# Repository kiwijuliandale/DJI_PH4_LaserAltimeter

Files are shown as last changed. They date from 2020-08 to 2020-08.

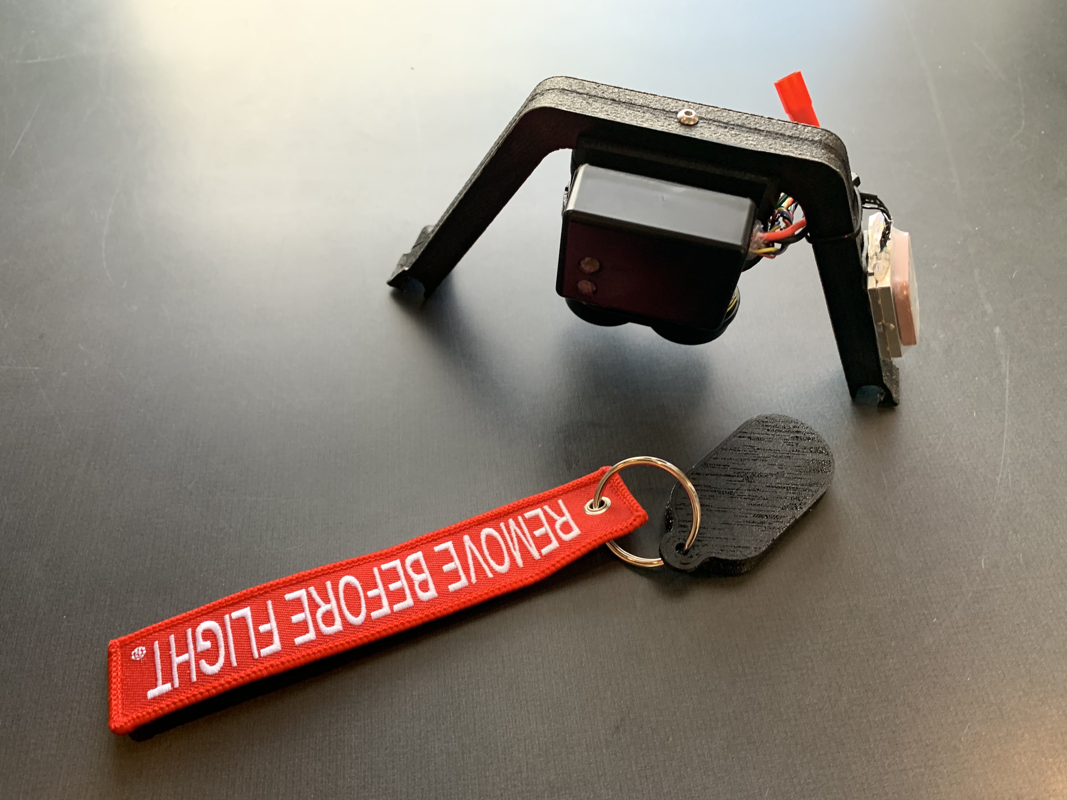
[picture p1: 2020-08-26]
Assembly/IMG_0025.jpeg

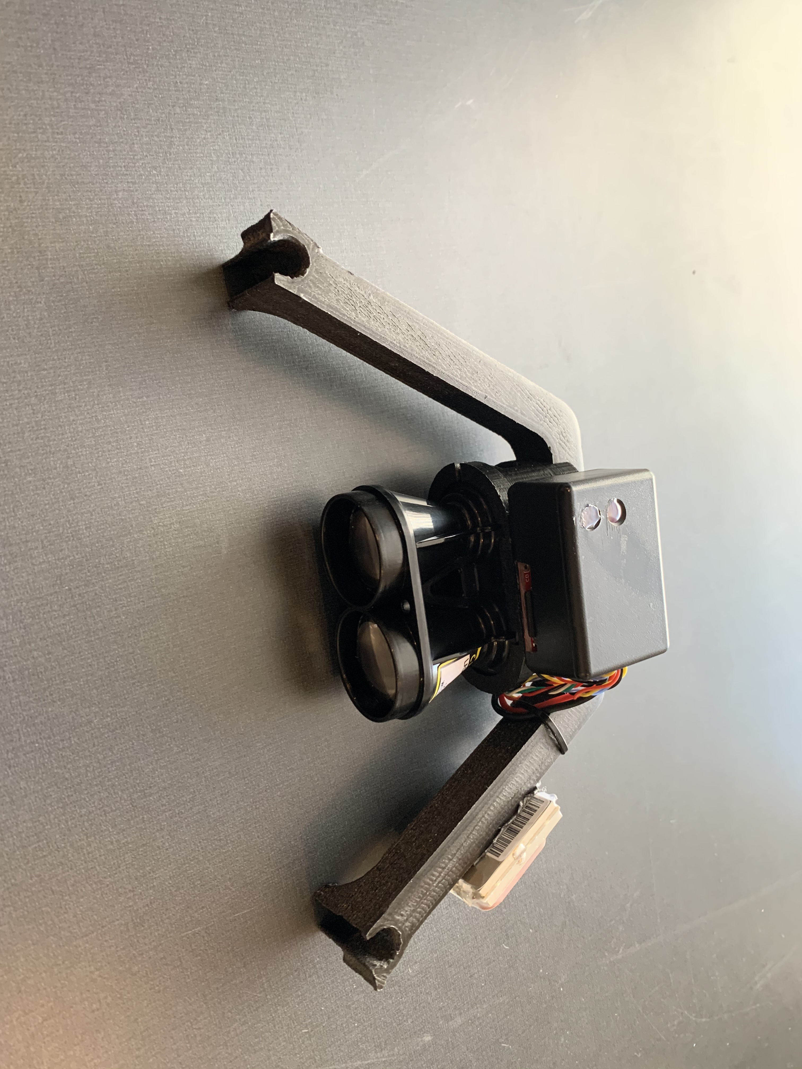
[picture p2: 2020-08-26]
Assembly/IMG_0023.jpeg

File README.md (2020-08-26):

# DJI Phantom 3/4 laser altimeter installation

Before we begin, there are some important warnings…

**WARNING** 
Modifying the DJI will void any warranties and could damage the aircraft. Only perform these modifications if you have adequate technical skills to 
perform the modifications.

**Disclaimer** 
The information provided by [Julian Dale or Duke University MaRRS Lab] (“we,” “us” or “our”) on [marineuas.net or Github/marrs-lab] (the “Site”) is for general informational purposes only. All information on the Site is provided in good faith, however we make no representation or warranty of any kind, express or implied, regarding the accuracy, adequacy, validity, reliability, availability or completeness of any information on the Site.

Under no circumstance shall we have any liability to you for any loss or damage of any kind incurred as a result of the use of the site or reliance on any information provided on the site. Your use of the site and your reliance on any information on the site is solely at your own risk. 

About the information included:

>I have included a tutorial video on how to install the power feed from the DJI battery. (By no means my best work but should provide the necessary information!!)
This allows the laser to power from the aircraft and will automatically start when the aircraft powers up. This saves weight and the risk of a separate power supply going flat. If you feel at all uncomfortable disassembling your aircraft, then use an external USB power bank or small LiPo battery. Please find the video tutorial here https://vimeo.com/451298704 

There are three folders containing ;

| Folder | Description |
| ------ | ------ |
| 3D Printer Files | STL's for printing the mouting frame |
| Arduino Code | Arduino code and libraries for the sensors. I have included the instructions from Steve Dawson & Hamish Bowman’s (Departments of Marine Science and Geology, University of Otago, Dunedin New Zealand) This is all their work and code and I have just included this as a reference |
| Assembly | Some assembly images and references. We have been using modified SF11C laser settings with good results over the water. Information on these settings are included in the assembly folder |

**Making Photogrammetry measurements:**
Because the laser altimeter is measuring a hypotenuse length, you need to calculate the vertical distance with a basic trig function. This can be done in excel.
Once this is done, KC Bierlich, Walter Torres and Clara Bird have developed some amazing tools for making the measurements in MorhhometriX and Collatrix for collating the data outputs. 
https://github.com/wingtorres/morphometrix
https://github.com/cbirdferrer/collatrix

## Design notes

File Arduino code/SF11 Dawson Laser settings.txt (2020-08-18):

     b: Zero datum offset ........ 0.00 m
     c: Measuring mode ........... long range
  ------------------------------------
  d: Hide communication menu
     e: Serial port baud rate..... 19200
     f: Serial output mode........ continuous
     g: I2C bus address........... 0x55
     s: Pixhawk I2C compatability. on
  ------------------------------------
  h: Show analog and alarm menu
  ------------------------------------
  m: Show filter menu
  ------------------------------------
  s: Show advanced menu
  ------------------------------------

     *** SF11/C V9 Firmware: V1.5.0 ***
            Serial: S11-16588

  ------------------------------------
  a: Hide system menu
     b: Zero datum offset ........ 0.00 m
     c: Measuring mode ........... long range
  ------------------------------------
  d: Hide communication menu
     e: Serial port baud rate..... 19200
     f: Serial output mode........ continuous
     g: I2C bus address........... 0x55
     s: Pixhawk I2C compatability. on
  ------------------------------------
  h: Hide analog and alarm menu
     i: Linear analog output...... 0.00 m to 25.00 m = 0.00 V to 2.048 V
     j: Analog distance range..... 0.00 m to 25.00 m
     k: Analog voltage range...... 0.00 V to 2.048 V
  ------------------------------------
  m: Show filter menu
  ------------------------------------
  s: Show advanced menu
  ------------------------------------

     *** SF11/C V9 Firmware: V1.5.0 ***
            Serial: S11-16588

  ------------------------------------
  a: Hide system menu
     b: Zero datum offset ........ 0.00 m
     c: Measuring mode ........... long range
  ------------------------------------
  d: Hide communication menu
     e: Serial port baud rate..... 19200
     f: Serial output mode........ continuous
     g: I2C bus address........... 0x55
     s: Pixhawk I2C compatability. on
  ------------------------------------
  h: Hide analog and alarm menu
     i: Linear analog output...... 0.00 m to 25.00 m = 0.00 V to 2.048 V
     j: Analog distance range..... 0.00 m to 25.00 m
     k: Analog voltage range...... 0.00 V to 2.048 V
  ------------------------------------
  m: Hide filter menu
     n: Output on lost signal..... 130.00 m
        p: Confirm lost signal.... 1.0 seconds
     q: Median filter............. on
        r: Median filter size..... 16 results
  ------------------------------------
  s: Show advanced menu
  ------------------------------------

     *** SF11/C V9 Firmware: V1.5.0 ***
            Serial: S11-16588

  ------------------------------------
  a: Hide system menu
     b: Zero datum offset ........ 0.00 m
     c: Measuring mode ........... long range
  ------------------------------------
  d: Hide communication menu
     e: Serial port baud rate..... 19200
     f: Serial output mode........ continuous
     g: I2C bus address........... 0x55
     s: Pixhawk I2C compatability. on
  ------------------------------------
  h: Hide analog and alarm menu
     i: Linear analog output...... 0.00 m to 25.00 m = 0.00 V to 2.048 V
     j: Analog distance range..... 0.00 m to 25.00 m
     k: Analog voltage range...... 0.00 V to 2.048 V
  ------------------------------------
  m: Hide filter menu
     n: Output on lost signal..... 130.00 m
        p: Confirm lost signal.... 1.0 seconds
     q: Median filter............. on
        r: Median filter size..... 16 results
  ------------------------------------
  s: Hide advanced menu
        t: Sensitivity offset..... 0
  ------------------------------------

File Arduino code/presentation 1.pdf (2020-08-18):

Building the LIDAR/GPS datalogger

This is a building guide intended as supplementary material to the manuscript “Inexpensive aerial photogrammetry for studies of whales and other large marine animals”. It is written to allow interested researchers to build the datalogger described in the manuscript. The building task is not difficult for anyone with reasonably good soldering skills.

Parts list
Item | Example supplier
Lightware SF11 lidar | www.lightware.co.za
3.3v 8MHz Pro Micro Arduino clone | www.sparkfun.com
3.3v ProMicro MicroSD transflash breakout | www.sparkfun.com
GlobalSat EM506 GPS module | www.sparkfun.com
Pololu MinIMU-9 v5 Gyro, Accel, Compass | www.nicegear.so.nz
DC-DC UBEC 5v 3a voltage regulator | www.mrpositive.co.nz
100µF capacitor | Any electronics store
microSD card | Any electronics store
7.4v 2cell LIPO batteries | Any R/C hobby store
Plus: wire, solder, heatshrink

The size and writing speed of the micro SD card are not critical, as the datalogger files are small (c.8kB/min).

You will need to figure out how long the cabling needs to be to suit your particular UAV and your preferred layout. You’ll also need to source appropriate plastic boxes to house the gps antenna and the datalogger. For the datalogger, we’ve used an Olympus microcassette box. A rubber band provides extra security to hold the lid shut.

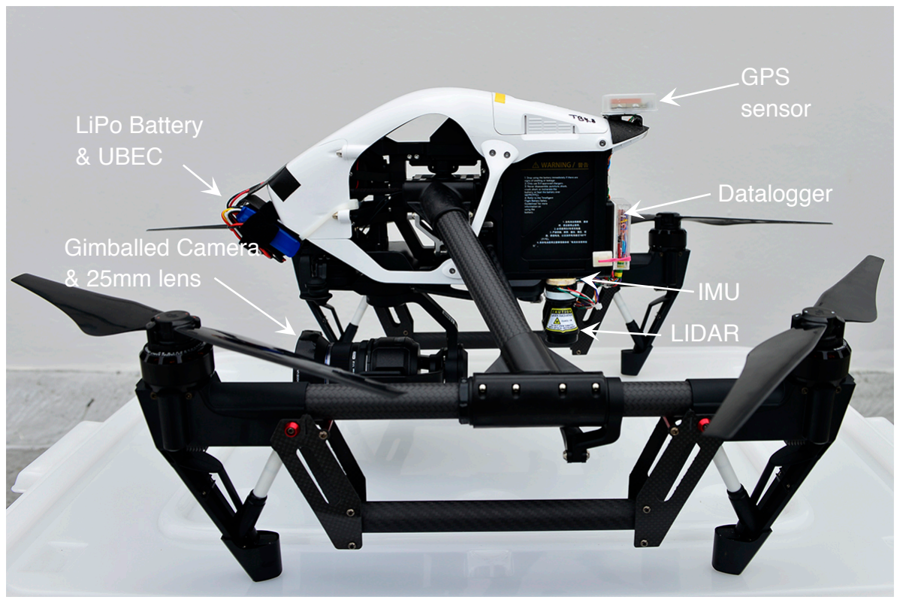
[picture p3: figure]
LiPo Battery & UBEC; GPS sensor; Datalogger; LIDAR; IMU; Gimballed Camera & 25mm lens

Layout of the datalogger components on the DJI Inspire 1Pro

Datalogger wiring diagram

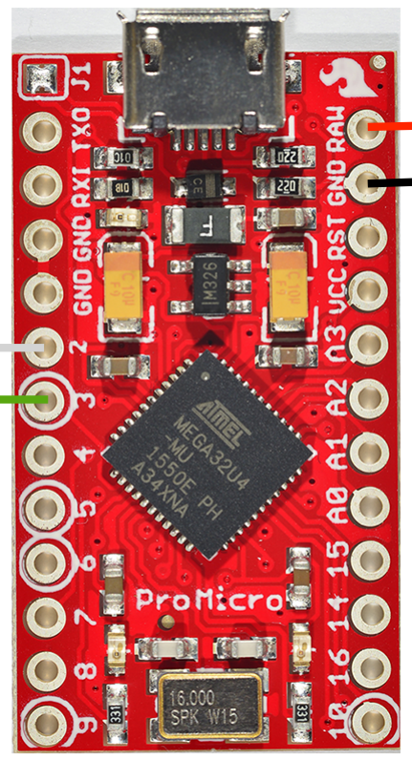
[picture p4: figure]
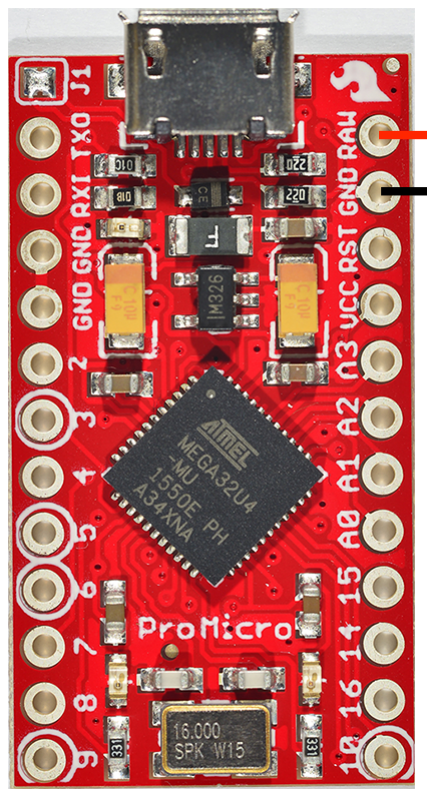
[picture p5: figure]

lidar
connector

UBEC +5v
UBEC Gnd

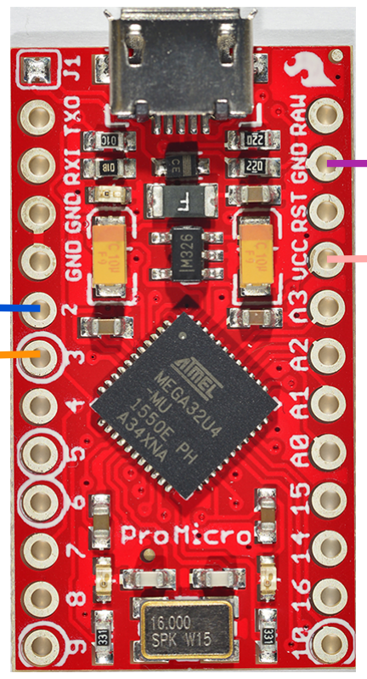
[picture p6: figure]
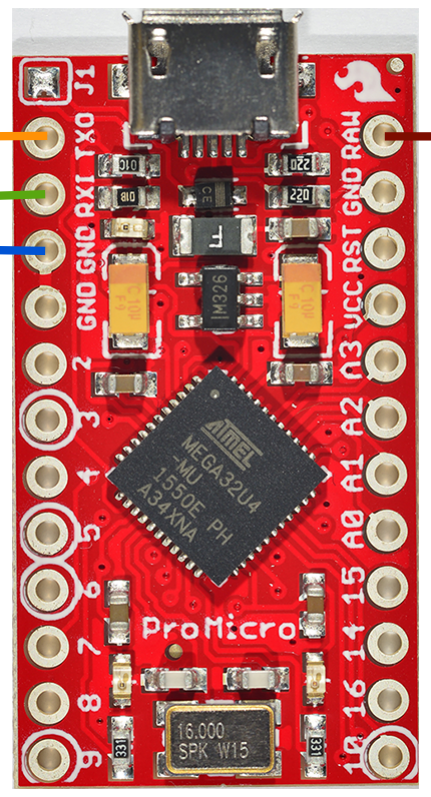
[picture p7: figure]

g
GPS
connector

MicroSD breakout

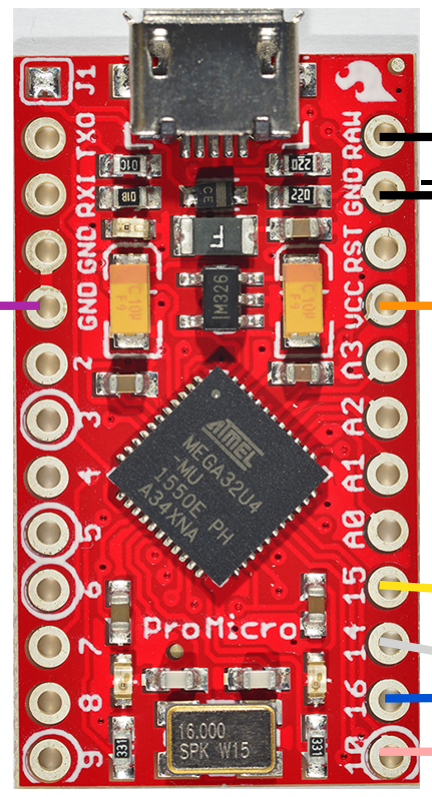
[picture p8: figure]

100µF -

MinIMU

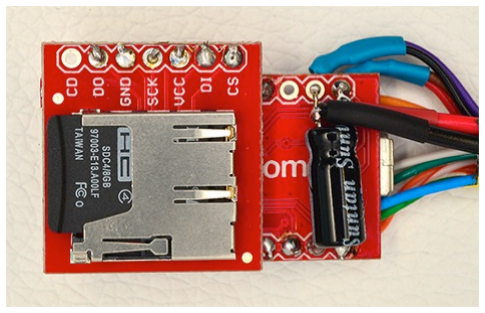
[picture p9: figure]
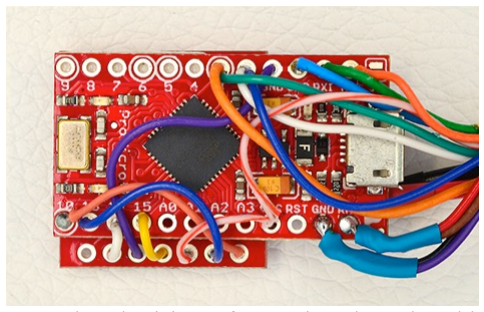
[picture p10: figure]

Completed wiring of ProMicro board and breakout

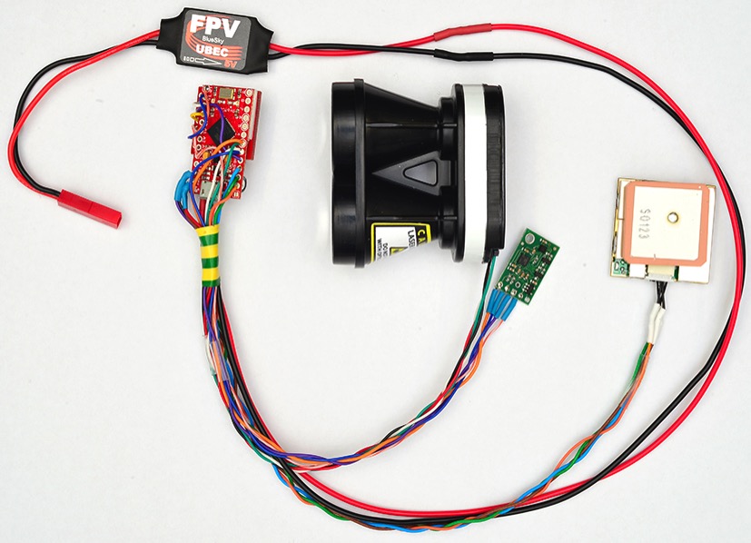
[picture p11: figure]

Completed assembly of component parts before attachment to UAV

Programming and setup of LiDAR + Datalogger

LiDAR setup (SF11C Laser Altimeter from Lightware Optoelectronics)
This needs to be set up using a micro-USB cable plugged in between your computer and the LiDAR unit. You will need a terminal program to do this, examples are the vendor-supplied Lightware Terminal on MS Windows, Zterm on Mac OS, or GTKTerm on Linux.

http://www.dalverson.com/zterm/
https://sourceforge.net/projects/gtkterm/

You will need to connect to the appropriate serial/COM port as created by the USB connection. If in doubt try several from the list. If using Z-Term, connect the cable to the lidar and plug it in to your computer before you start Z-term, Under Settings/Modem Preferences choose the “usbserial….” port, and under Settings/Connection set baud rate to 115200 (8 bits 1 stop bit). You should see a live stream of data. If not, try changing the baud rate.

Pressing the space bar stops the live stream, and brings up the LiDAR setup menu. Input the following settings. Press the appropriate letter to expand the menu.

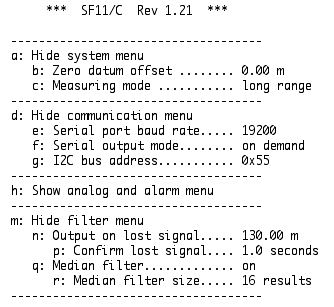
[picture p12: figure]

For the median filter we use a window size of 16. As the device samples at 16 Hz this corresponds to a 1 second filter window. This setting makes the lidar much less sensitive to momentary interruptions of the beam, and produces far fewer outliers.

Serial baud rate (d, e) is not relevant. The I2C protocol (d, g) is crucial.

Arduino software
We used the Arduino IDE software version 1.6.12 with a SparkFun 3.3v ProMicro Arduino board

In the Tools menu go to: Tools -> Board -> Board manager...

Find "SparkFun AVR Boards" and click install.

After that finished, in the Tools menu go to:
Tools -> Board -> SparkFun Pro Micro
Tools -> Processor -> ATmega32U4 (3.3V, 8 MHz)
Tools -> Port -> (select appropriate value once it is plugged in)

It is important that the correct values are set for the above.

You will need to install the TinyGPS++ processing library from http://arduiniana.org/libraries/tinygpsplus/
Follow the instructions on the website to download the library andinstall it into your Arduino "libraries" folder.

For inclinometer support using the Pololu MinIMU-9 board, install the LSM6 library
from https://github.com/pololu/lsm6-arduino
Follow the instructions on the website to download the library and install it into your Arduino "libraries" folder.

With the drone_GPS_and_LiDAR_logger_with_accel.ino and support_fns.ino files installed in a folder named "drone_GPS_and_LiDAR_logger_with_accel" within your Arduino "sketchbook" folder, select File -> Open in the Arduino IDE and then run Sketch -> Verify/Compile. An error will occur if the wrong family of Arduino board is selected or if it can't find the support libraries where it expects to find them on the hard drive.

Finally, with the Arduino connected and the appropriate serial Port selected from the Tools menu, select Sketch -> Upload. This will re-compile the code and upload it via the USB cable. Lights on the Arduino will blink during the process. When it is complete the words "Done uploading." will appear near the bottom of the Arduino software window.

To test, select Tools -> Serial Monitor from the menu. New data will only be
output when a valid GPS fix is in place.

Before Installation on the UAV we glue the flat side of IMU to the rear of the lidar, and make up a lightweight spacer to glue the LIDAR underneath the UAV. We attempt to do this as near to the centre of balance as we can.

Installation on the UAV
We made carbon fibre brackets for the GPS sensor and to hold the battery and UBEC on the I1P. Something less sophisticated should suffice.

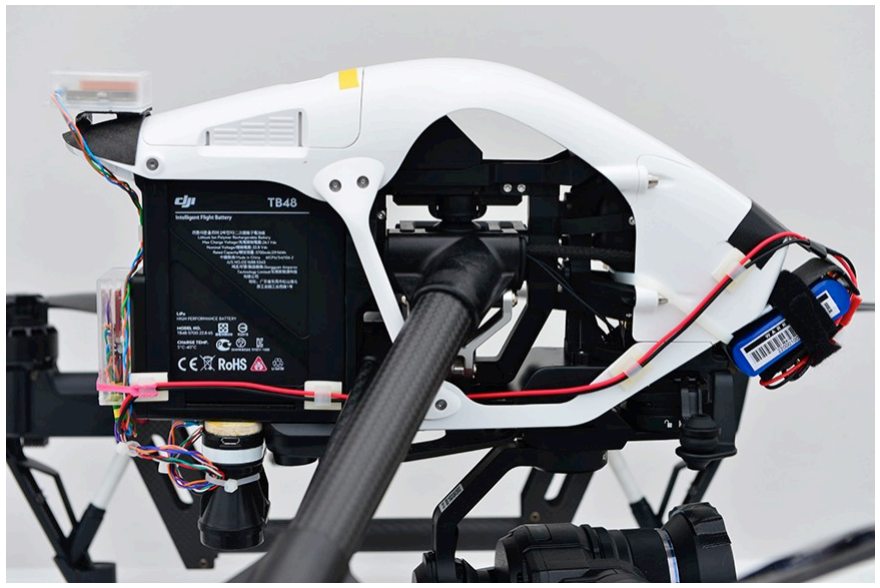
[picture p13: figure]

Wires can be held out of the way with adhesive cable clips, and/or tucked inside the body work of the UAV.

Running the datalogger
Connecting the battery starts the the datalogger. It needs to have a GPS fix in order to write data. A red LED will light up on the GPS and on the datalogger board. Once it gets a fix, you’ll see red flashes on the GPS as it sends a data string. The datalogger flashes green once a second when it's writing a new line of data, and flashes amber when it flushes the data to the microSD card.

A 500 mAh battery will last several hours. We change or charge after 4 hours or so. We disconnect it if not flying for more than a few minutes.

The datalogger files are .csv files. The easiest way to open them is to open a blank Excel sheet, and use File/Import. Note that the times are GMT. To delete these files off the chip, you must delete, and empty the trash. The file header is self explanatory.

Happy flying!

________
Steve Dawson¹ & Hamish Bowman² Departments of Marine Science¹ and Geology² University of Otago, Dunedin New Zealand

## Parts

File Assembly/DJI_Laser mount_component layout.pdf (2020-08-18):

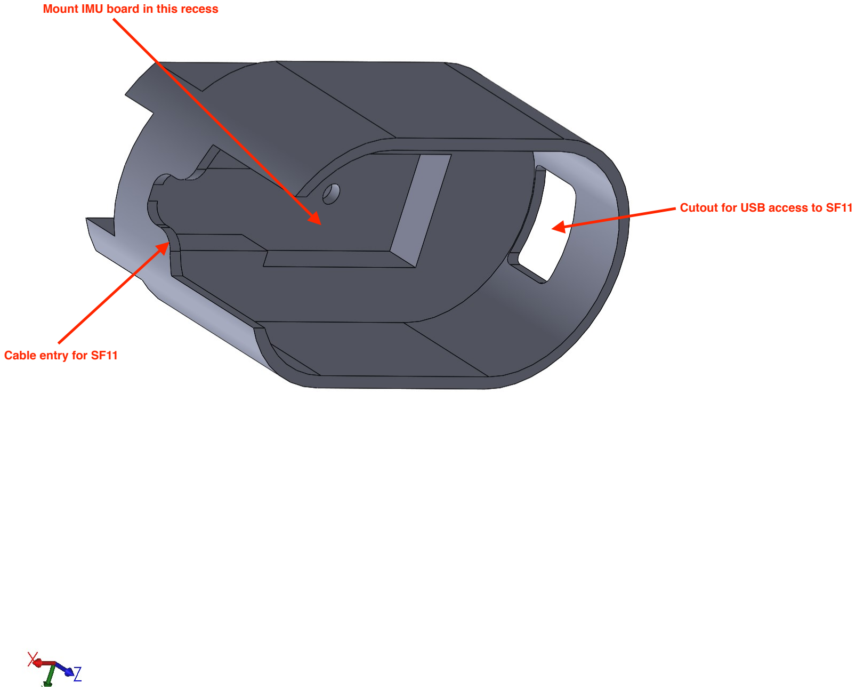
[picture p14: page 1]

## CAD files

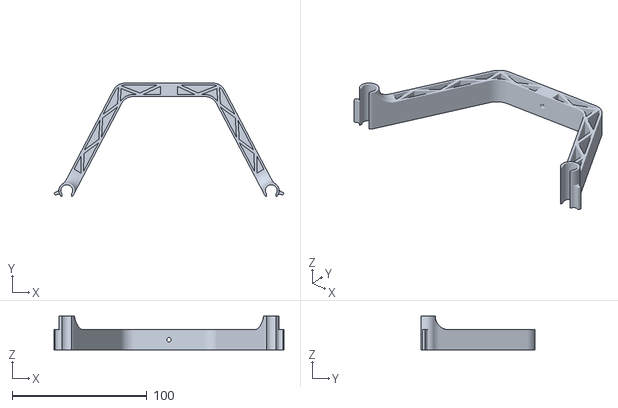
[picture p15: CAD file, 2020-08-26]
3D Printer files/DJI_P4_LegMount.STL
171.0 x 84.7 x 25.0

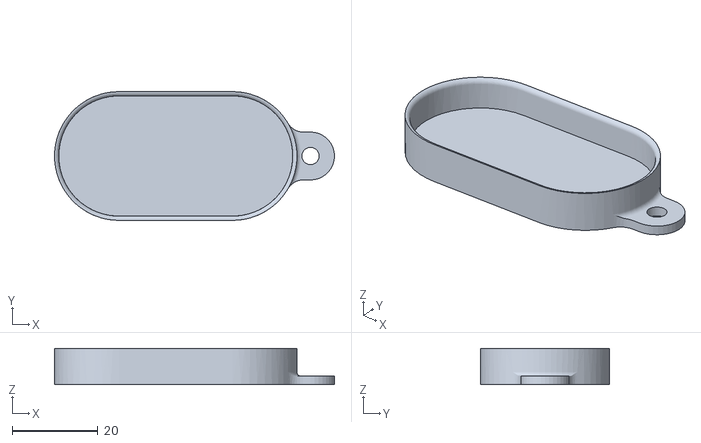
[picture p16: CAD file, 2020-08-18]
3D Printer files/Lens cover v2.0.STL
65.2 x 30.0 x 8.50

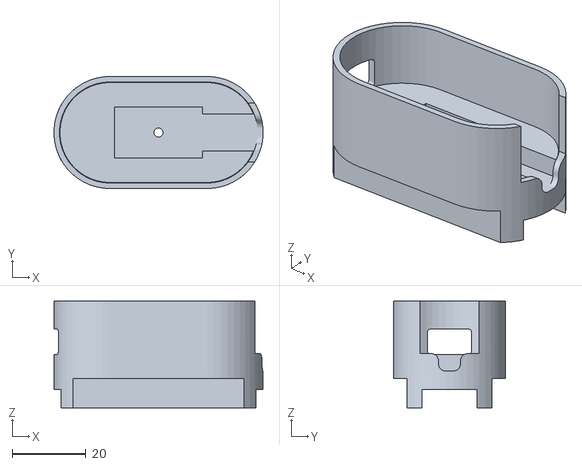
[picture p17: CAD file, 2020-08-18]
3D Printer files/DJI Frame laser mount_2.5mmhole_V2.STL
56.8 x 30.5 x 29.0

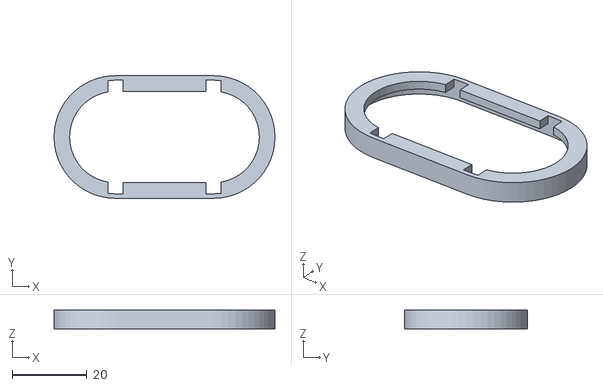
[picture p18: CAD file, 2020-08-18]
3D Printer files/SF11 Retaining ring.STL
59.3 x 32.9 x 5.00

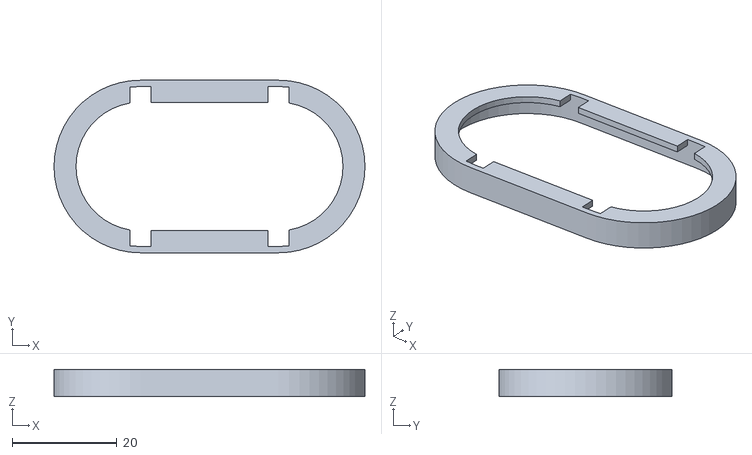
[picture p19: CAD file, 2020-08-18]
3D Printer files/SF11 laser retainer ringV1.STL
59.3 x 32.9 x 5.20

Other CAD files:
3D Printer files/DJI Frame laser mount_nut recess_V2.STL

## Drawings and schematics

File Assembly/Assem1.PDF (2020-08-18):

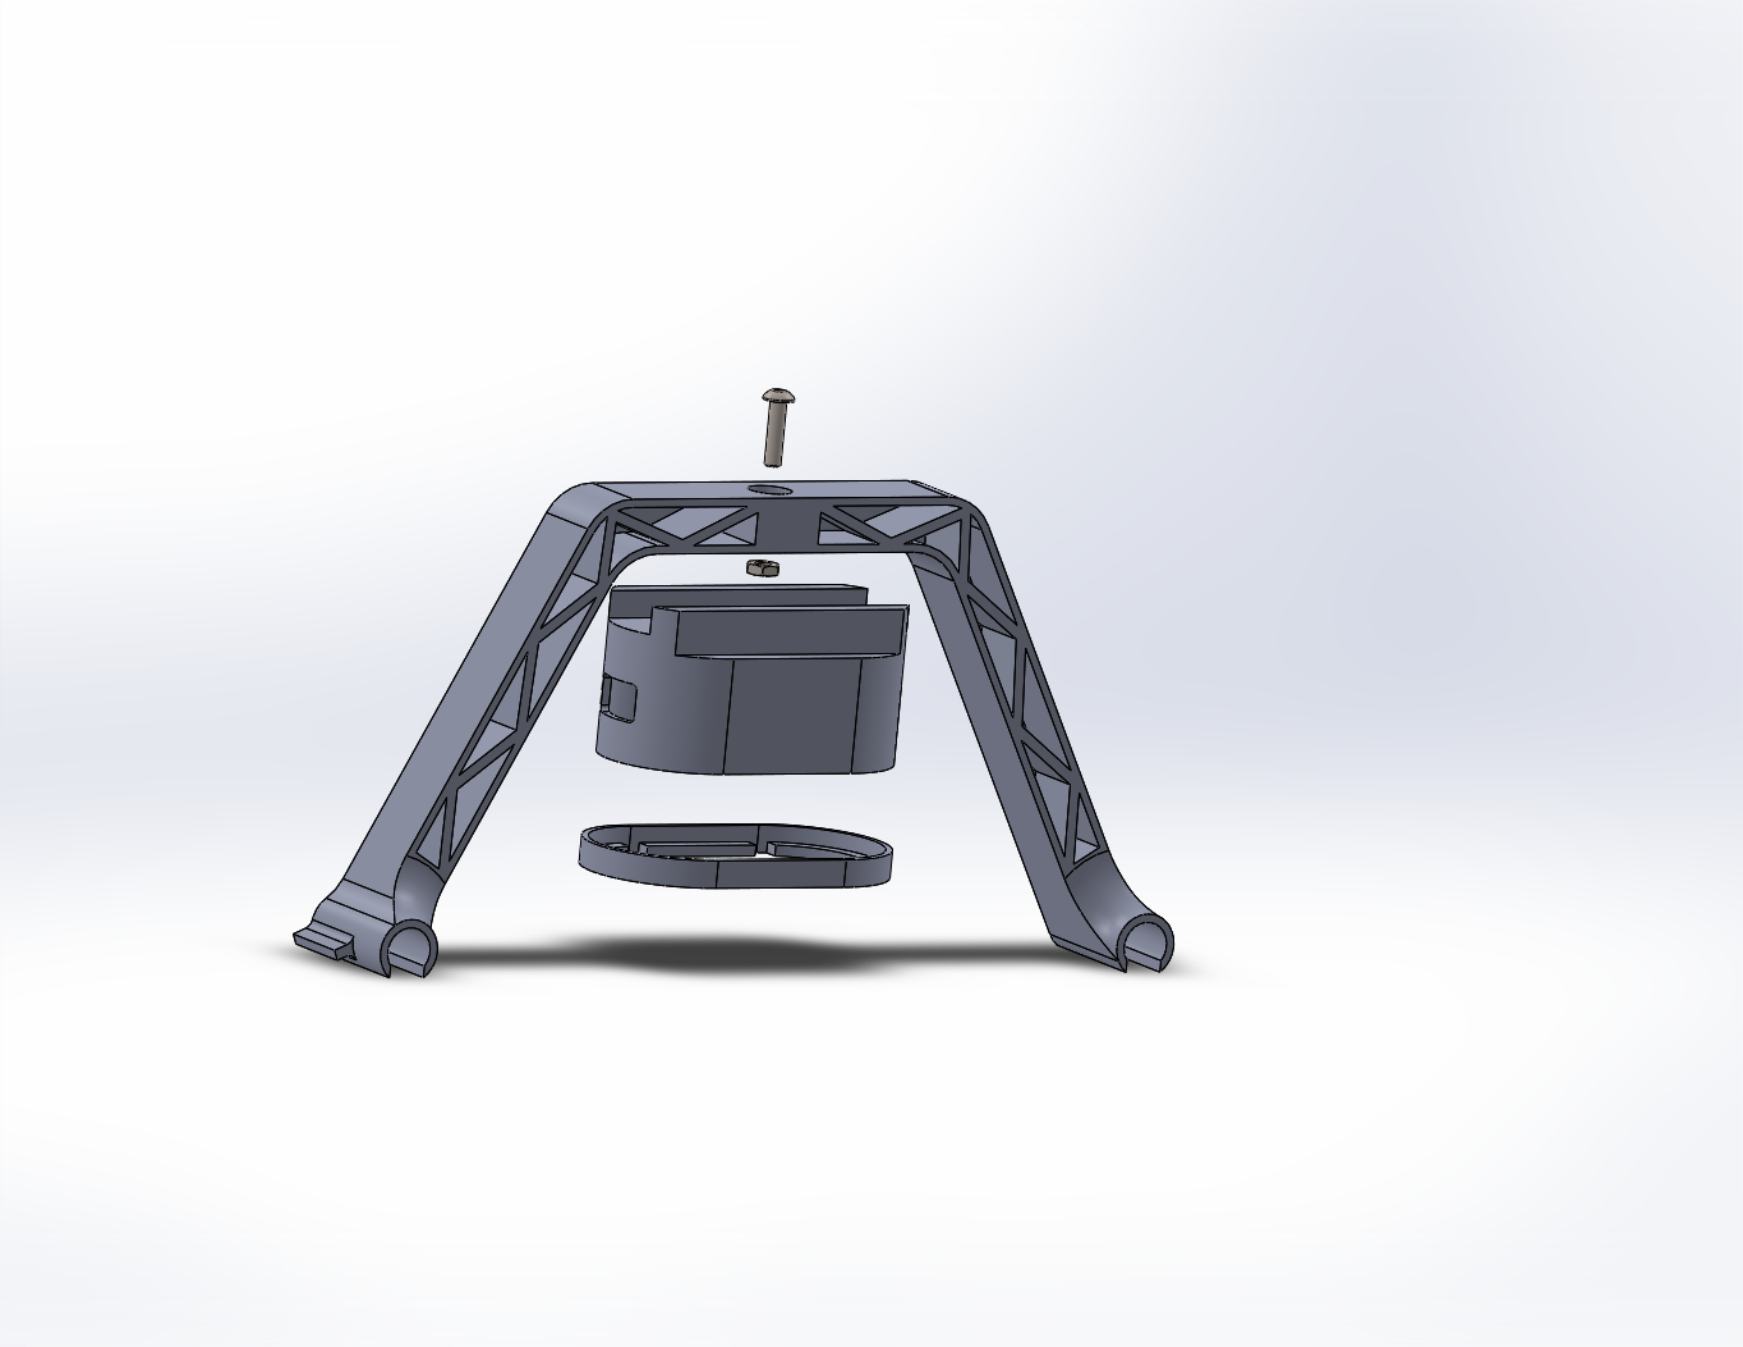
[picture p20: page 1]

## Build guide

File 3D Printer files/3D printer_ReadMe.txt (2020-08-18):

3D Printer Notes

Lens Cover.STL = Printed in TPU for flexible push fit

DJI_P4_LegMount-1.STL = Printed in NylonX of similar. If using ABS or TPEG you may need to adjust shell thickness and infill to allow enough flex for the part to snap ontp the landing gear securely.

SF11 laser retainer ringV1.STL = Printed in ABS. Use a small spot of supeglue on several points around the laser mount to hold the laser in place once assembled.

*DJI Frame laser mount_2.5mmhole_V2.STL = Printed in ABS. This verison can be tapped out to M3. Secure the laser mount to the frame mount with a M3 x 12mm button head cap screw.
Alternativly
*DJI Frame laser mount_nut recess_V2.STL = Printed in ABS. This version has an M3 nut cutout within the model. You will need to put a pause point in the slicing file to allow the nut to be inserted in the recess and then continue printing the layer abover the hole to encapsulate the nut. Secure the laser mount to the frame mount with a M3 x 12mm button head cap screw.

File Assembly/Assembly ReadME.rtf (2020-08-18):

Assembly Notes.

⁃ Mount IMU in printed mount bracket and then install SF11 Laser
⁃ The Arduino board and SD card holder can be heat-shrink wrapped and mounted using 3M outdoor mounting tape. Alternatively a small enclosure can be used to house the electronics.
⁃ Mount the GPS antenna on the leg mount with a clear view of the sky using 3M outdoor mounting tape.
⁃ Change the settings on the SF11 as describes in the SF11C over water settings.pdf

**Ensure all vision positioning sensors are deactivated on the Aircraft as the laser obscures them and will cause un-characteristic flight behaviours**

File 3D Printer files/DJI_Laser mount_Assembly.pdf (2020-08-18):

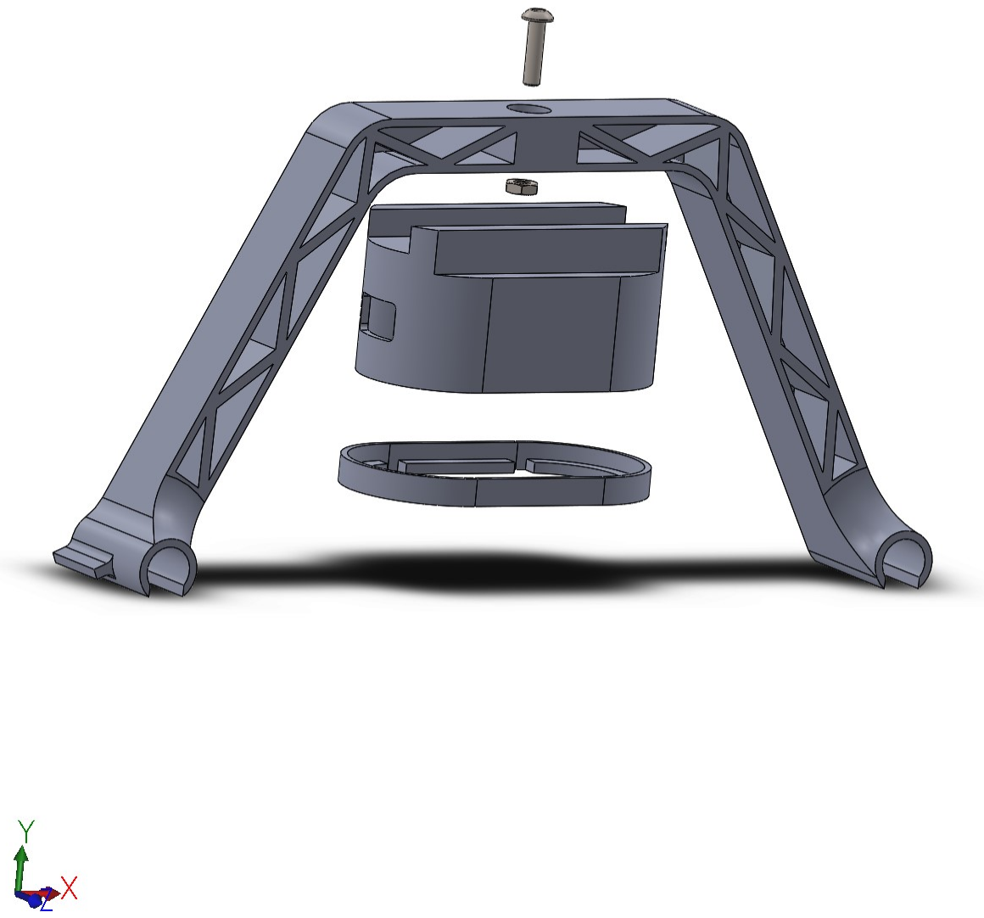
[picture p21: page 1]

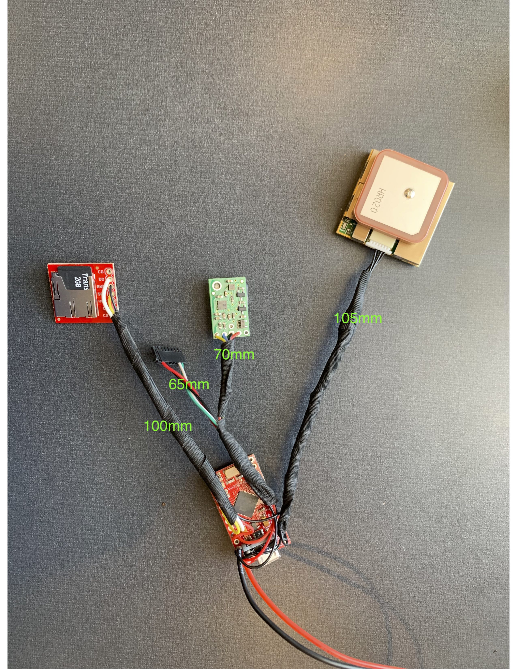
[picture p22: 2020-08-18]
Assembly/Cable lengths for DJI phantom mounting.jpg

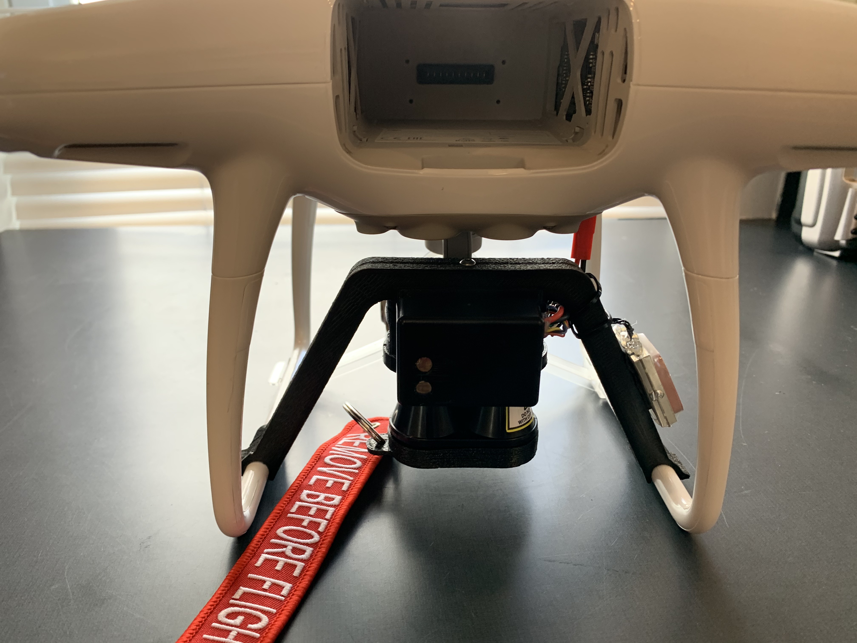
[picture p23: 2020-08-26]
Assembly/IMG_0028.jpeg

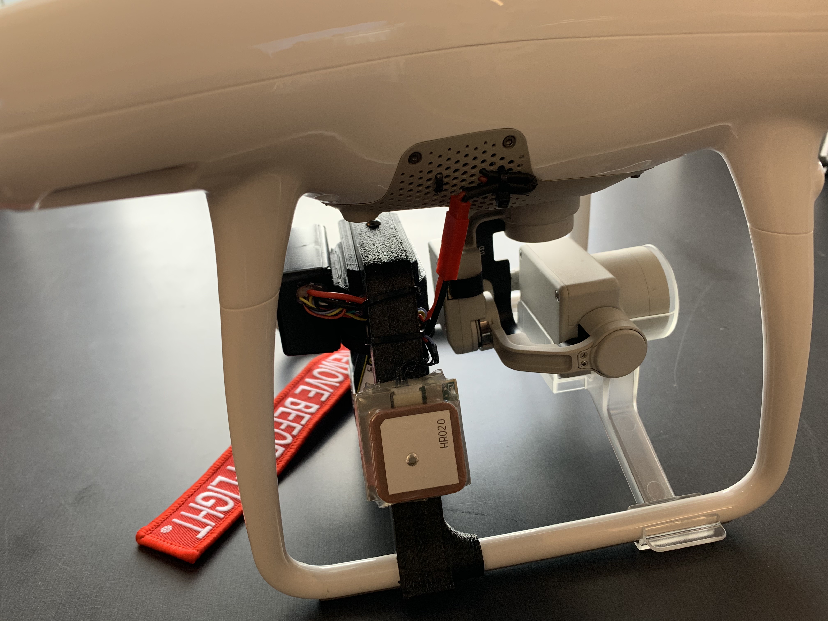
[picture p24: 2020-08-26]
Assembly/IMG_0027.jpeg

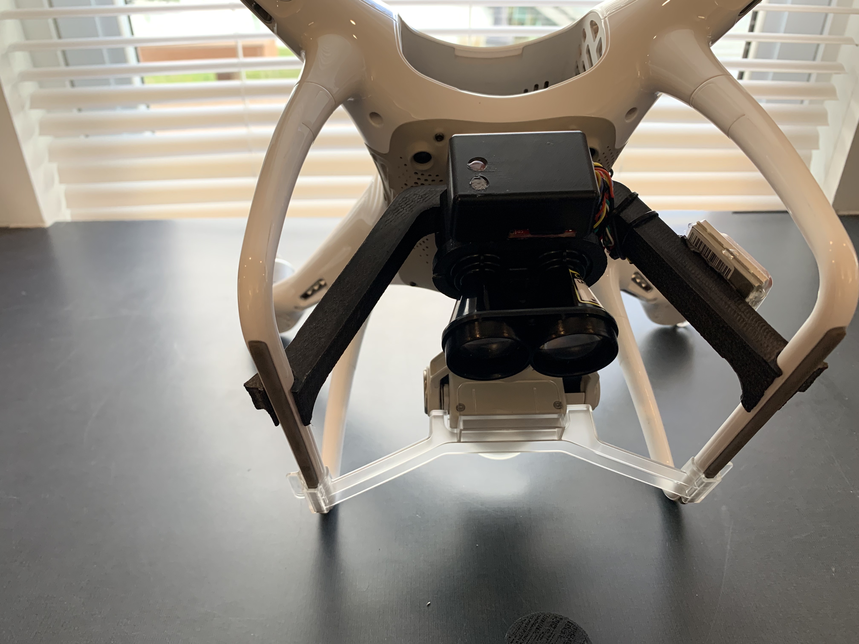
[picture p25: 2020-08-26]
Assembly/IMG_0029.jpeg

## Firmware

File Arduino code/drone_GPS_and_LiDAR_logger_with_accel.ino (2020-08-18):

// Program to talk to GlobalSat EM-506 GPS and lightware SF-11 laser rangefinder
// and log to SparkFun SDcard board.
// HB 14 June 2016     (added IMU code 19 May 2017)

/*
GPS hardware:
 Hardware serial Rx,Tx are on pins 0,1 on the ProMicro, but 'Serial1' already
 knows that.  The serial Rx LED is pin 17 and can be used independently, the
 Tx pin needs to be treated differently- see the ProMicro hookup guide example.

 The GPS doesn't seem to have a long memory and resets its programming after
 being off for a couple days. So it seems that we have to reprogram it at
 startup. I'd like to have it at 19200 baud instead of the default of 4800
 but rerunning Serial1.begin() after reprogramming the baud rate and then
 sleeping for 1 sec doesn't seem to work well and is probably too risky to
 trust anyway.
    Serial1.print("$PSRF100,1,19200,8,1,0*38\r\n");   // set baud rate to 19200, N81
    Serial1.print("$PSRF100,1,9600,8,1,0*0D\r\n");    // set baud rate to 9600, N81
    Serial1.print("$PSRF100,1,4800,8,1,0*0E\r\n");    // set baud rate to 4800, N81

    Serial1.begin(19200);
    delay(1000);


 State machine:  (incompatible with always listening to the GPS stream, see below)
    unsigned long prev_millisec = 0;
    long interval = 1000;
    ...
    unsigned long current_millisec;
    // wait a minimum of 1 second between iterations
    current_millisec = millis();
    if(current_millisec - prev_millisec < interval)
        return;    //  (->low power mode?)

    prev_millisec = current_millisec;
    Serial.println(".");


GPS library:
  TinyGPS++ (LGPL>=2.1)  http://arduiniana.org/libraries/tinygpsplus/
  Because the GPS is always coming in and the input buffer on the UART is
  only 64 bytes(?), we can't just delay() or go to sleep between outputs,
  we constantly have to read() & digest the NMEA sentences coming in. The
  TinyGPS++ examples have a smartDelay() function to aid with this.

  The "isValid" result is refering to the last checksum **NOT** the GPS fix.
  The "isUpdated" result is true if a new valid (both checksum and fix) NMEA
  message has come through and the memory field has been touched since the
  last time you QUERIED it. So the date fields will be "updated" once per
  second by $GPRMC, not once per day when the date changes.
  Use the "age()" result to query for the last good fix (1500 ms is suggested).

  TinyGPS++ mainly works on GGA and RMC, so we turn off the other NMEA sentences.

  Lat/Lon floating point values are restricted to 32bit precision; so a total
  of 7 or 8 significant digits including those before the decimal point.
  1e-5 * 1852 * 60 = 1.11 meters.  The GPS unit outputs decimal minutes to
  0.0001 precision, (0.0001 / 60) * 1852 * 60 =  0.18520 meters. The TinyGPS++
  library gives us "raw" billionths of a degree output we can reassemble later.
  [ Perhaps use the NeoGPS library for better precision?
     https://github.com/SlashDevin/NeoGPS ]


LiDAR:
 I2C SDA,CLK on the ProMicro are pins 2 and 3. The unit is preprogrammed at
 the 7-bit address 0x55. It returns two bytes of data to make the integer
 number of centimeters distance. The result is ordered big-endian.
    ////// get laser value //////
    // get 2 bytes from the SF-11 range finder
    Wire.requestFrom(I2C_ADR, 2);
    if (Wire.available() >= 2) {
        byteH = Wire.read();
        byteL = Wire.read();
        // combine in big endian order
        distance_cm = byteH * 256 + byteL;
        Serial.print("\tlidar (cm): ");
        Serial.println(distance_cm);
    }

SDcard:
 The SD card should be formatted using the SD card foundation's official formatting
 tool. Note the SDcard reader must be fed 3.3v for VCC, as 5v will damage it.


IMU:
  Pololu MinIMU-9 v5  www.pololu.com
  """ LIS3MDL mag sensor: (unused) """
  """LSM6DS33 gyro and accel sensor:
  The sensor outputs provided by the library are the raw
  16-bit values obtained by concatenating the 8-bit high and
  low accelerometer and gyro data registers. They can be
  converted to units of g and dps (degrees per second) using
  the conversion factors specified in the datasheet for your
  particular device and full scale setting (gain).

  Example: An LSM6DS33 gives an accelerometer Z axis reading
  of 16276 with its default full scale setting of +/- 2 g. The
  LA_So specification in the LSM6DS33 datasheet (page 11)
  states a conversion factor of 0.061 mg/LSB (least
  significant bit) at this FS setting, so the raw reading of
  16276 corresponds to 16276 * 0.061 = 992.8 mg = 0.9928 g.
  """
*/

#include <SPI.h>
#include <Wire.h>    // Wire.h provides I2C bus
#include <TinyGPS++.h>
#include <LSM6.h>
#include "SD.h"


#define USB_CONNECTED


// LiDAR I2C pins
//#define I2C_SDA  2
//#define I2C_CLK  3
#define I2C_ADR  0x55

// SDcard SPI pins
#define SPI_CS   10
//#define SPI_CLK  15
//#define SPI_MISO 14
//#define SPI_MOSI 16
#define RX_LED   17


// The TinyGPS++ object
TinyGPSPlus gps;


#define NUMSAMPLES 100    // for 400 it takes approx 0.852sec/cycle; 100 samples take 0.212 sec.

// IMU sensor
LSM6 imu;


// write out to sd card at least every 60 seconds
unsigned long prev_millisec = 0;
long interval = 60000;


// the logging file
File logfile;



////////////////////////////////////////////////////////////

int freeRam () {
    extern int __heap_start, *__brkval;
    int v;
    return (int) &v - (__brkval == 0 ? (int) &__heap_start : (int) __brkval);
}

////////////////////////////////////////////////////////////


void setup(void)
{

#ifdef USB_CONNECTED
    //// Start the USB-serial, for debugging
    Serial.begin(9600);
    /** Careful with this next line, if computer isn't attatched it will hang **/
    while(!Serial) {   // loop while ProMicro takes a moment to get itself together
        if (millis() > 6000)   // give up waiting for USB cable plugin after 6 sec
            break;
    }

    Serial.print(F("Free RAM: "));
    Serial.println(freeRam());
#endif

    //// GPS is on the ProMicro's UART (Serial1)
    Serial1.begin(4800);
    while(!Serial1);   // wait for it   (** NOTE this will hang the logger if GPS is not connected **)
    // Turn off messages we don't want
    Serial1.print(F("$PSRF103,02,00,00,01*26\r\n"));      // GSA off
    delay(20);
    Serial1.print(F("$PSRF103,03,00,00,01*27\r\n"));      // GSV off
    delay(20);

    //// startup I2C bus for the LiDAR
    Wire.begin();


    //// init LSM6 portion of IMU board
    if (!imu.init()) {
#ifdef USB_CONNECTED
        Serial.println("Failed to detect and initialize IMU!");
#endif
        lock_and_blink();  // lock it up
    }
    imu.enableDefault();


    /////////////////////////////////////////
#ifdef USB_CONNECTED
    Serial.print(F("Initializing SD card..."));
#endif
    // see if the card is present and can be initialized:
    if (!SD.begin(SPI_CS)) {
#ifdef USB_CONNECTED
        Serial.println(F("ERROR: SD card failed, or not present. Halting."));
#endif
        lock_and_blink();  // lock it up
        //or,  return;
    }
#ifdef USB_CONNECTED
    Serial.println(F("SD card initialized."));
#endif


/* TODO: set once we have GPS lock
    // set SD file date time callback function
    SdFile::dateTimeCallback(FileDateTime);
*/

    // create a new file
    char filename[] = "LOG_0000.CSV";
    //char filename[] = "LOGB0000.CSV";
    for (uint16_t i = 0; i < 10000; i++) {
        filename[4] = i / 1000 + '0';
        filename[5] = (i % 1000) / 100 + '0';
        filename[6] = (i % 100) / 10 + '0';
        filename[7] = i % 10 + '0';
        //Serial.print("Trying ");
        //Serial.println(filename);
        if (! SD.exists(filename)) {
            // only open a new file if it doesn't exist
            logfile = SD.open(filename, FILE_WRITE); 
            break;  // leave the loop!
        }
        //else {   // tidy up
        //   SD.remove(filename);
        //}
    }

    delay(500); // give it a chance to catch up before testing if it's ok.
    if (! logfile) {
#ifdef USB_CONNECTED
        Serial.println(F("ERROR: couldn't create log file. Halting"));
#endif
        lock_and_blink();  // lock it up
    }

#ifdef USB_CONNECTED
    Serial.print(F("Logging to: "));
    Serial.println(filename);
    Serial.println();

    ////////////////////////////////////

    Serial.println(F("# GPS and Laser Rangefinder logging with Pro Micro Arduino 3.3v"));
    Serial.println(F("# units:  accel=1g  gyro=deg/sec"));

    Serial.print(F("#gmt_date\tgmt_time\tnum_sats\tlongitude\tlatitude\t"));
    Serial.print(F("gps_altitude_m\tSOG_kt\tCOG\tHDOP\tlaser_altitude_cm\t"));
    Serial.println(F("tilt_deg\taccel_x\taccel_y\taccel_z\tgyro_x\tgyro_y\tgyro_z"));
#endif
    logfile.println(F("# GPS and Laser Rangefinder logging with Pro Micro Arduino 3.3v"));
    //logfile.println(F("#  Datalogger unit 'B'"));
    logfile.println(F("# units:  accel=1g  gyro=deg/sec"));

    logfile.print(F("#gmt_date\tgmt_time\tnum_sats\tlongitude\tlatitude\t"));
    logfile.print(F("gps_altitude_m\tSOG_kt\tCOG\tHDOP\tlaser_altitude_cm\t"));
    logfile.println(F("tilt_deg\taccel_x\taccel_y\taccel_z\tgyro_x\tgyro_y\tgyro_z"));
    logfile.flush();

    // should we wait a while for GPS to get a fix?
    wakeful_sleep(2000);

    // blink 10 times, we're good to go
    for (int i = 0; i < 10; i++) {
        digitalWrite(RX_LED, LOW);
        TXLED1;
        wakeful_sleep(100);
        digitalWrite(RX_LED, HIGH);
        TXLED0;
        wakeful_sleep(100);
    }
}


///////////////////////////////////////////////////

struct imu_data {
    float Grav_x;
    float Grav_y;
    float Grav_z;
    float Gyro_x;
    float Gyro_y;
    float Gyro_z;
    float tilt_deg;
};


void loop(void)
{

#ifdef DEBUG_NMEA
    // Echo GPS to USB-serial port for debugging:
    char c = 'x';    //gps
    while(Serial1.available() > 0) {
        c = Serial1.read();
        if(c == '\r')
            continue;
        else if(c == '\n')
            Serial.println();
        else
            Serial.print(c);
    }
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

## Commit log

2020-08-18 Initial files upload
    [Assem1.SLDASM, DJI Frame laser mountV2.3.SLDPRT, DJI Frame laser mount_2.5mmhole_V2.3.SLDPRT, DJI Frame laser mount_2.5mmhole_V2.STL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]
2020-08-18 clean up
    removed temp files
    [Lens cover v2.0.STL]
